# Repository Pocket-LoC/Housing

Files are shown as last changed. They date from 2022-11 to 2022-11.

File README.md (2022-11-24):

# Pocket LoC
 
Lab-on-chip (LoC) technology is becoming increasingly relevant, especially in the field of medicine. However, often LoC setups rely on complex lab equipment for operation. The aim of this project is to create an affordable and portable LoC setup as a proof-of-concept for truly pocket-sized LoC - the Pocket LoC.

Pocket LoC can be assembled with standard equipment found in a typcial engineering lab (such as a maker space or FabLab). Once assembled, Pocket LoC is fully portable and only needs a PC to operate.

## Housing
This repository contains the design files and instructions for the Pocket LoC housing as well as the assembly instructions and parts lists required for the complete setup.

Feel free to contact me if you interested in a complete Pocket LoC device.

### 3D-printed parts
The housing is designed for 3D-printing. Although many different options for materials and printer settings are possible, I achieved best results using PETG with a layer height of 0.2mm on an 'Original Prusa i3 MK3S+'. Most standard 3D-printers and materials (e.g. PLA or ABS) should work, although some adjustments of part tolerances may be necessary.

The housing was designed in FreeCAD ([CAD folder](https://github.com/Pocket-LoC/Housing/tree/main/CAD)). Ready-to-print models (.stl) can also be found in the CAD folder. All parts can be printed without support structures.

### List of parts and tools
- 3D-printer
- dark, opaque printing filament (e.g. [black PETG](https://www.prusa3d.com/product/prusament-petg-jet-black-1kg/)) (approx. 30€)
- [Pocket LoC Sensor](https://github.com/Pocket-LoC/Sensor) (approx. 65-90€)
- [Pocket LoC Pump Controller](https://github.com/Pocket-LoC/Pump-Controller) (approx. 50-75€)
- Metal rod or nail (approx. 1.7mm diameter) for the hinge
- 4x [Bartels mp6-liq Micropumps](https://darwin-microfluidics.com/collections/piezo-pumps/products/bartels-mp6-micropump) (128€)
- [Bartels Pump Driver](https://darwin-microfluidics.com/collections/piezo-pumps/products/mp-highdriver4-pump-driver) (159€)
- [Tubing](https://darwin-microfluidics.com/collections/silicone-tygon-tubing/products/mp-t-1-3-mm-tygon-tubing-for-bartels-micropumps) (9.50€)
- 4x [Luer Adapters](https://darwin-microfluidics.com/collections/luer-fittings/products/barbed-to-female-luer-adapter-for-1-16-1-8-and-3-32-id-soft-walled-tubing-pack-of-10?variant=32430390018184) (11.40€ for 10)
- 4x 3ml Syringes as reservoir (approx. 10€ for 100)
- [Microfluidic Chip](https://github.com/Pocket-LoC/Chip) (approx. 250€ for many chips)
- Tweezers

In total the Pocket LoC costs about 600-800€, depending on the choice of materials and manufacturers. The costs scale significantly lower for larger quantities.

### Assembly
1.  Print the housing parts found in the CAD folder:
      - Base
      - Lid
      - Reservoir holder
      - Reservoir fixation block (4x)
      - Chip fixation block (2x)
      - Sensor cover
      
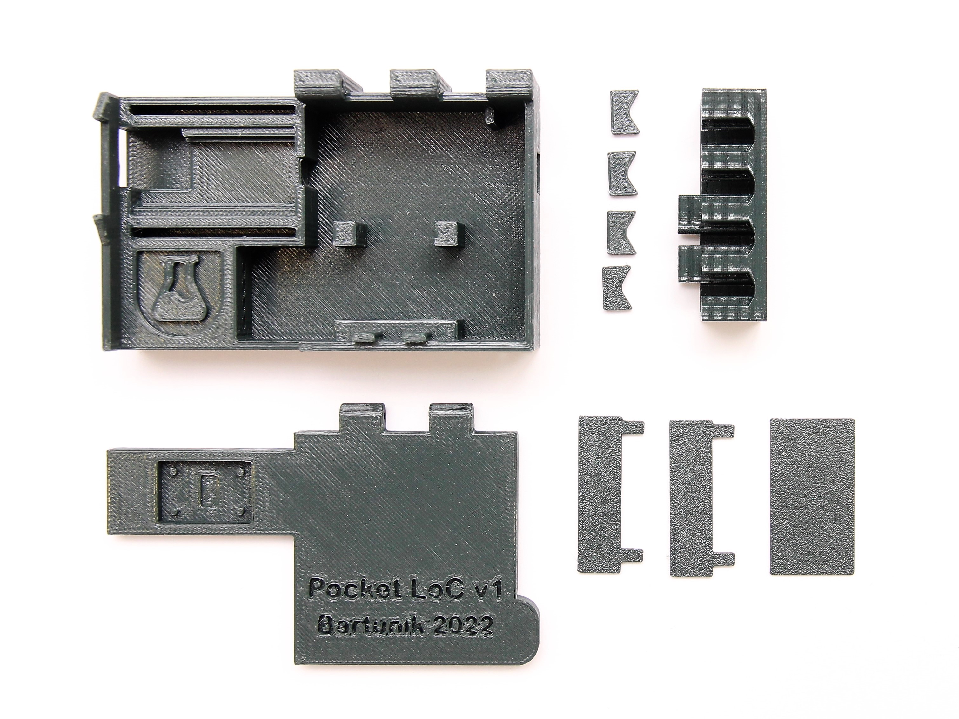
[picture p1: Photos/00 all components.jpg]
      
   
2. Fold the FFC as shown, about 25mm from one end and insert it into the connector on the LED PCB (part of the Pocket LoC sensor). Ensure the contacts of the FFC are facing outwards and the latch of the connector is properly fixed.

      <p float="left">
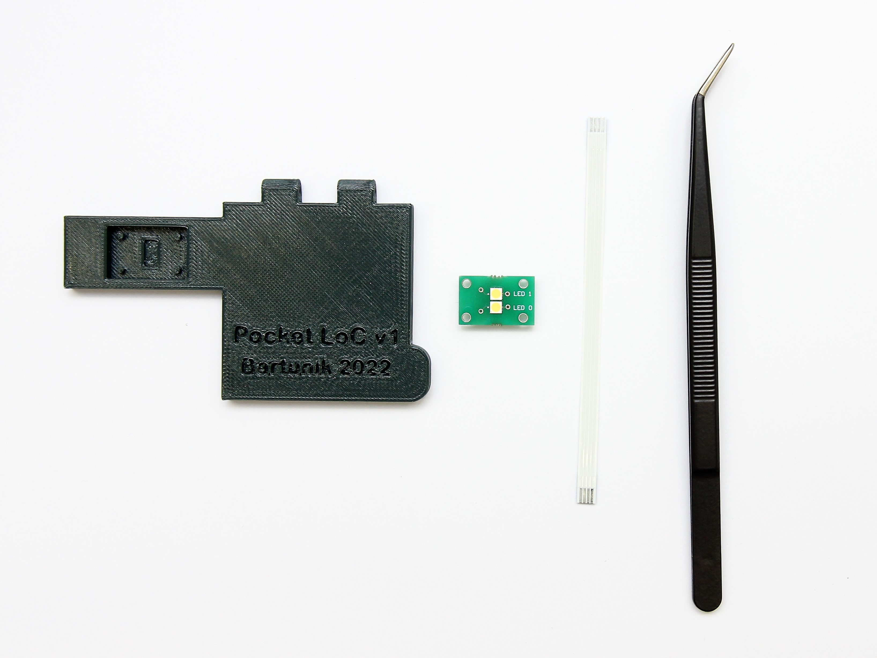
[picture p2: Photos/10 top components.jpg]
        
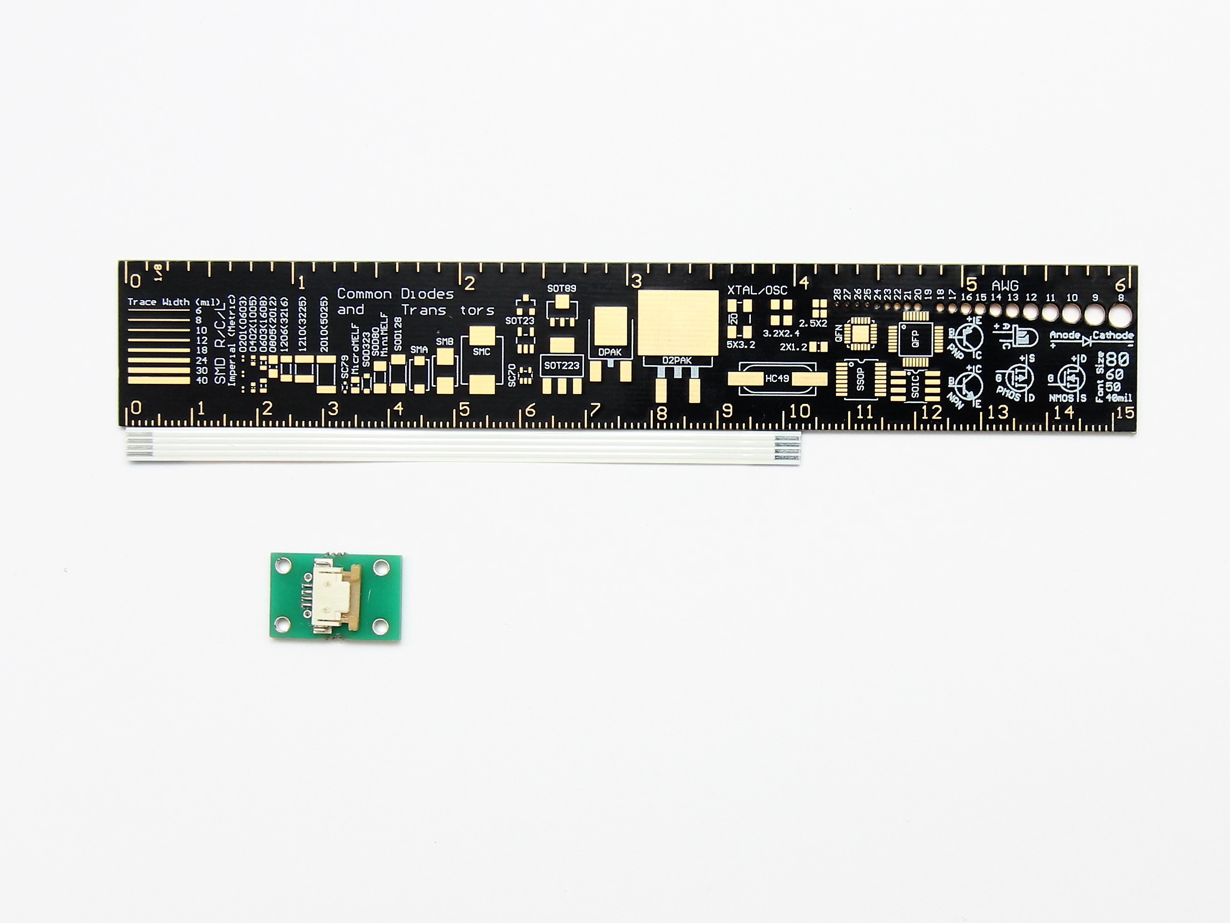
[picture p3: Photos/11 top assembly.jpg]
         
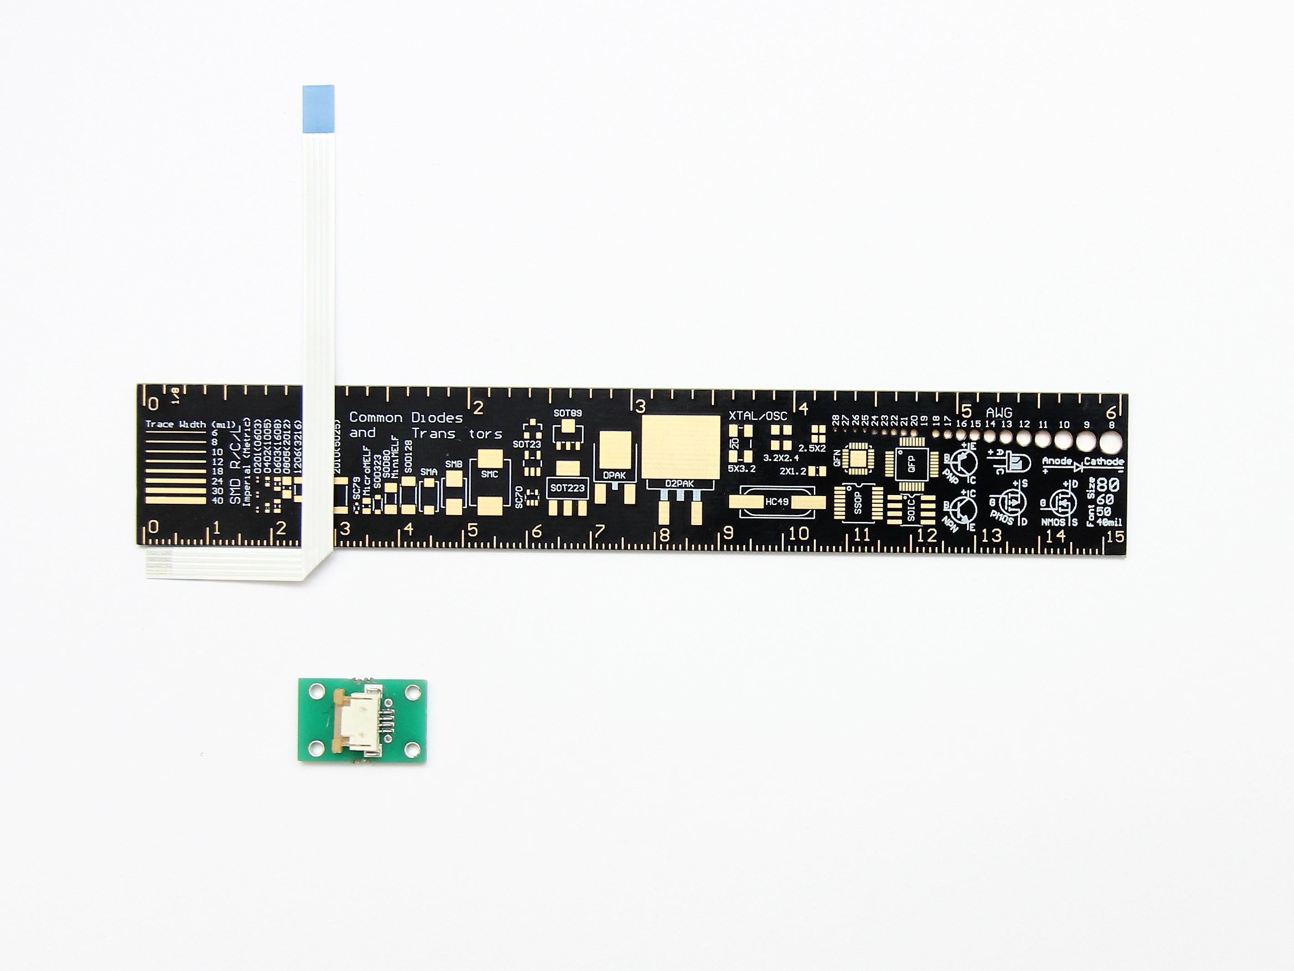
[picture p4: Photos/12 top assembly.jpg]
        
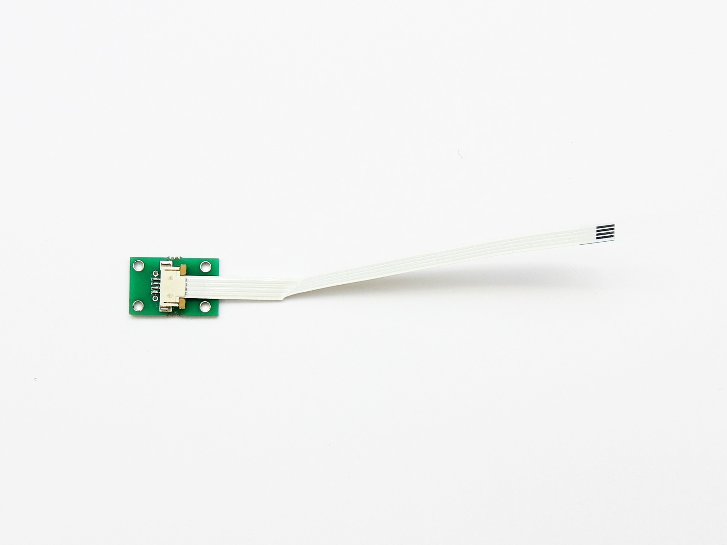
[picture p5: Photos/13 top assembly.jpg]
        
      </p>

3. Place the LED PCB in the top, threading the FFC through the hole and underneath the two holding bars. Tweezers may help with the last section.
      <p float="left">
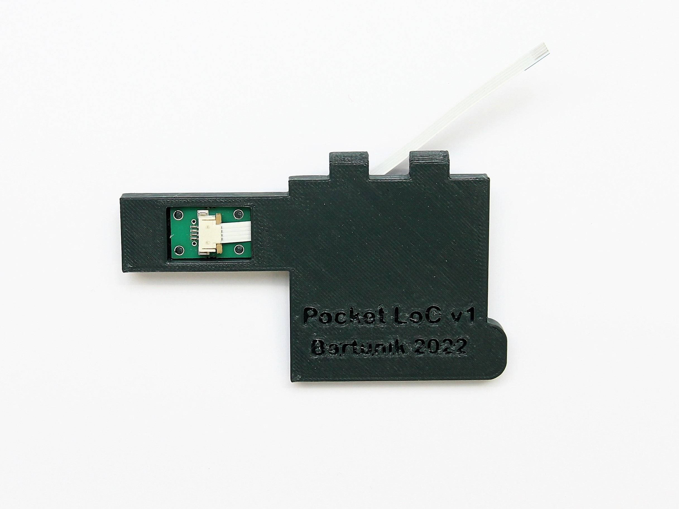
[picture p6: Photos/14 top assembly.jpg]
        
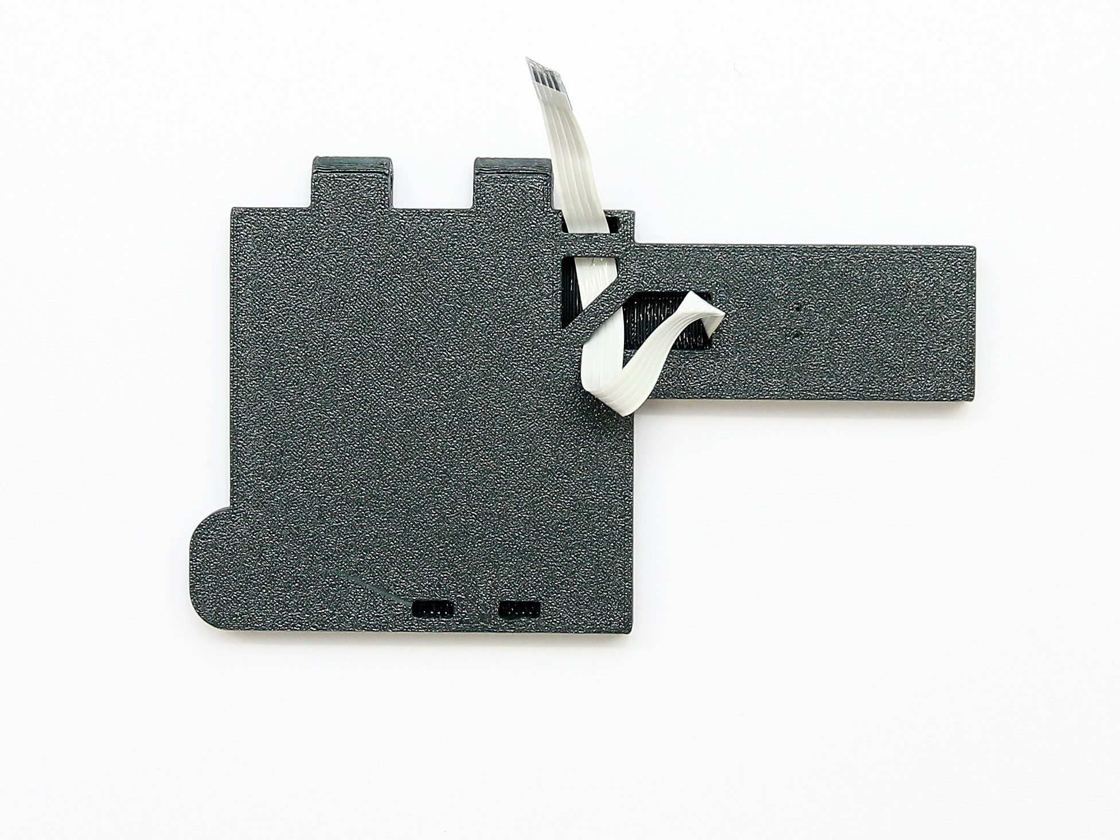
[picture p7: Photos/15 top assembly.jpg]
         
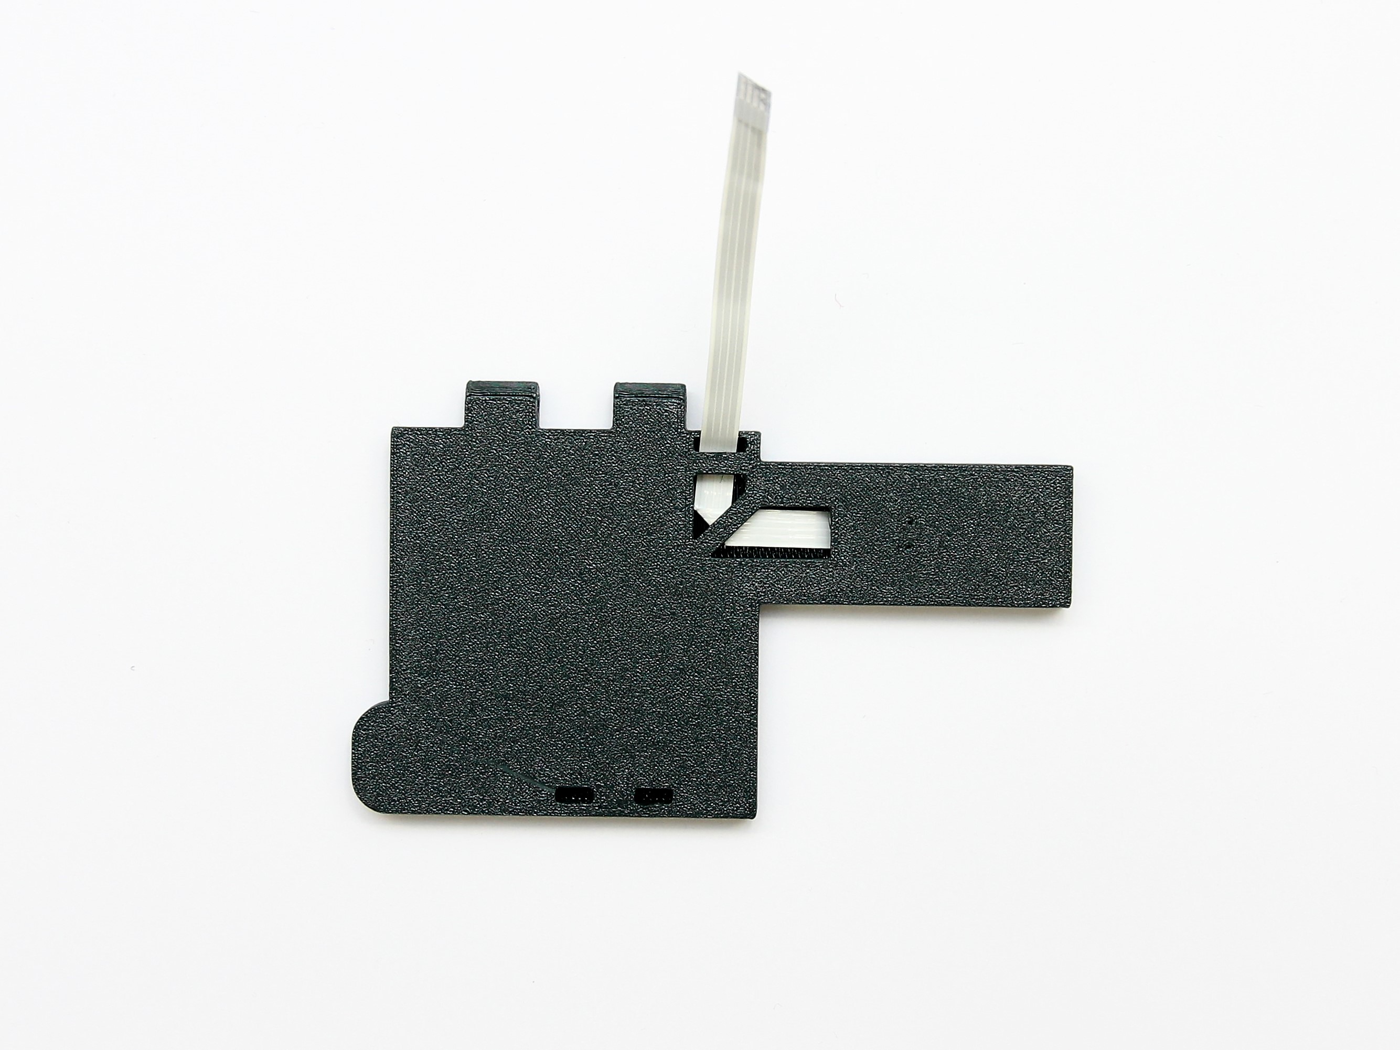
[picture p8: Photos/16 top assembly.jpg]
        
      </p>

4. Fold over the contact section of the FFC end. Then add a second fold, producing a Z-shape, at approx. 10 mm from the previous crease. Fold the FFC over at a right angle directly next to the last fold. Finally, add a crease approx. 15 mm from the outer edge of the angled fold. The folded FFC should look similar to the last picture.

      <p float="left">
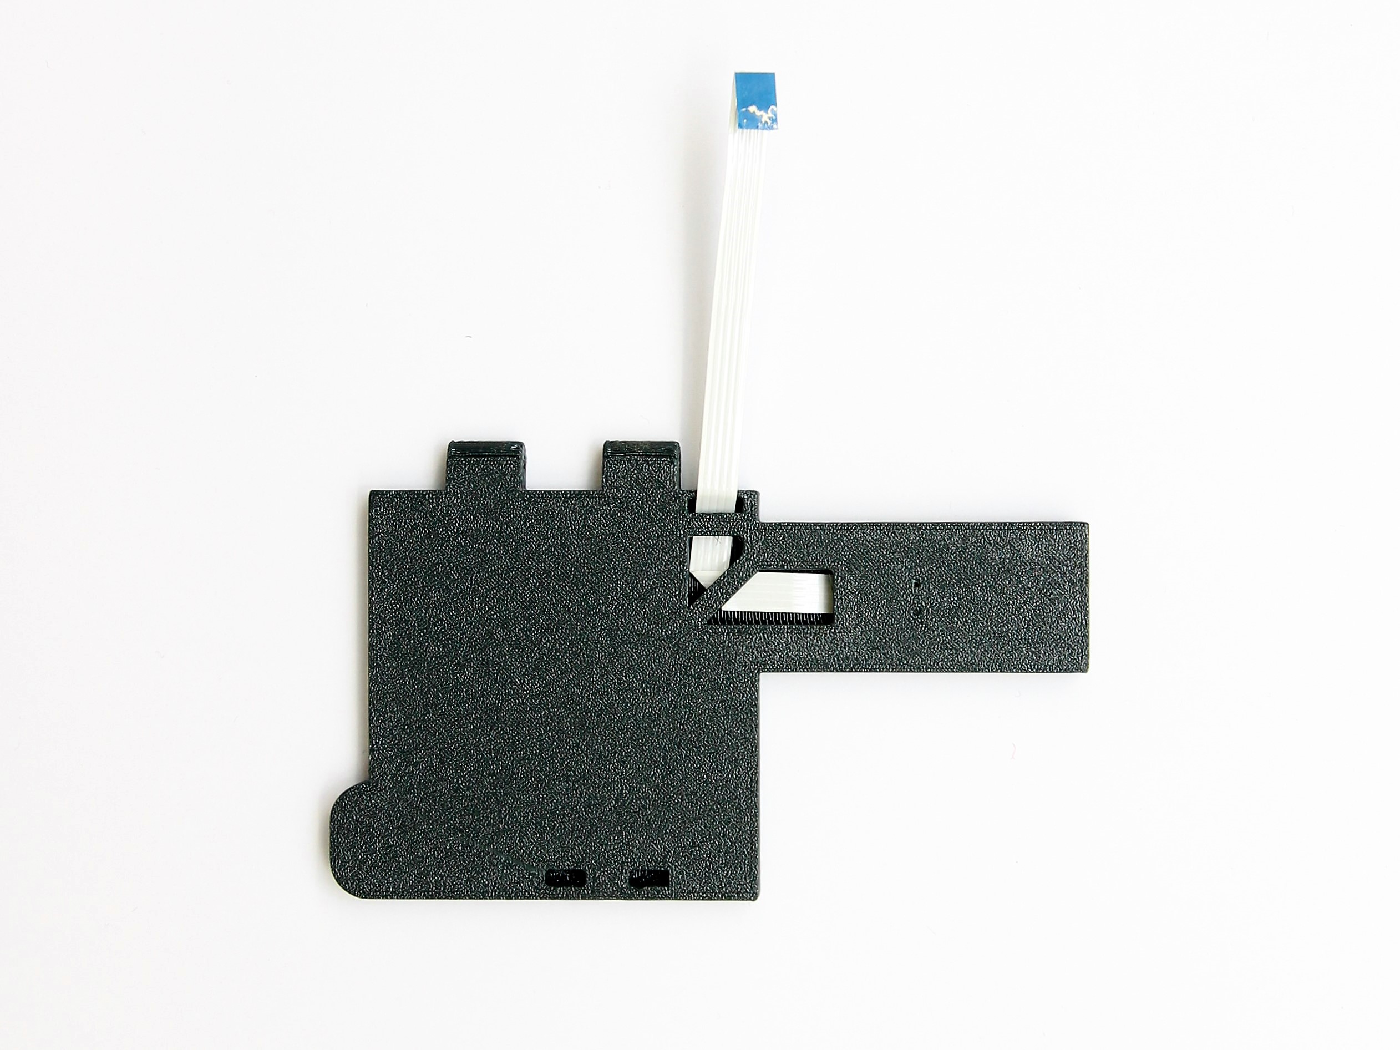
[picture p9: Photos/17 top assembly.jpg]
        
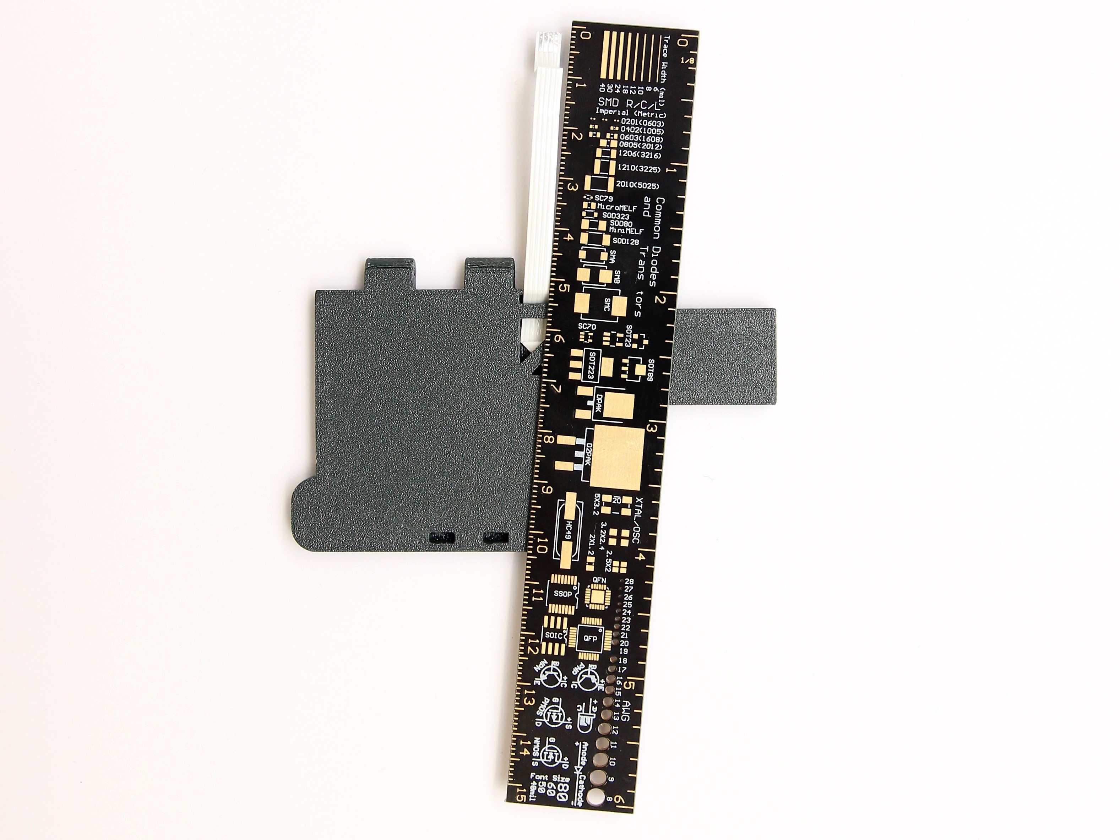
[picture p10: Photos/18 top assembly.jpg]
         
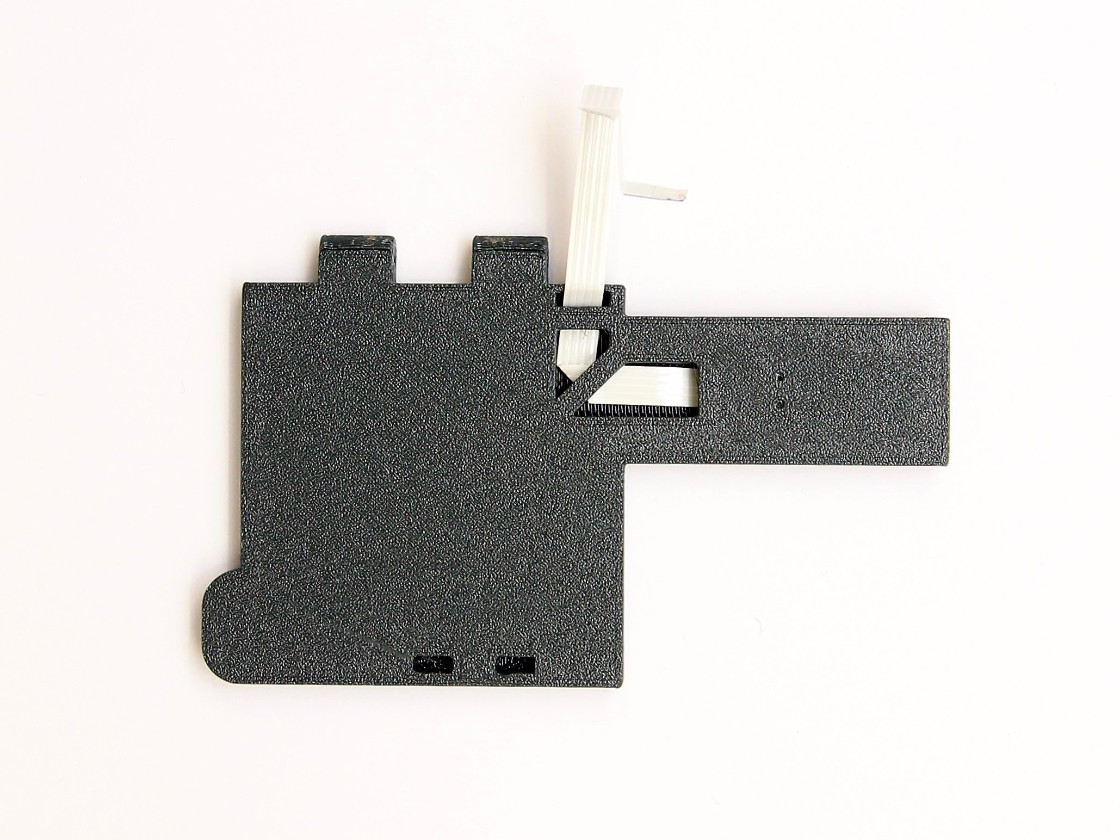
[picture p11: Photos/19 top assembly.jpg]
        
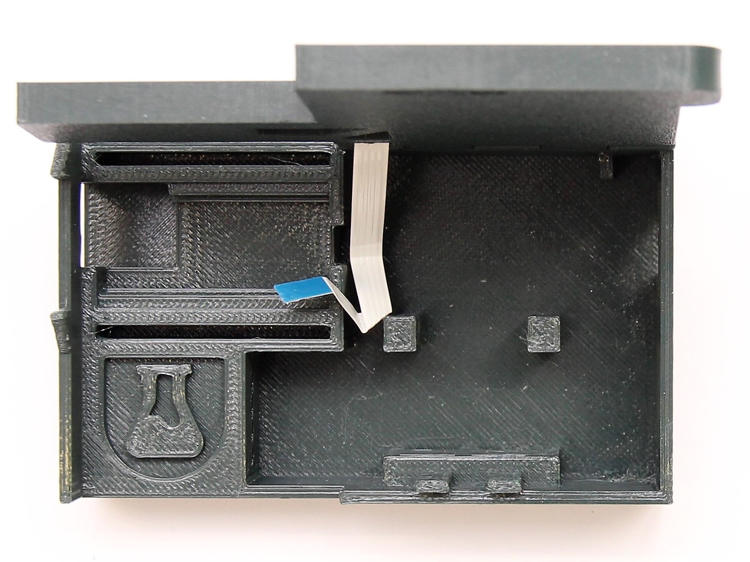
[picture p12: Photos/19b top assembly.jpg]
        
      </p>

5. Connect the base and lid by inserting the rod into the hinge section. A vice may help to push the rod in carefully.

      <p float="left">
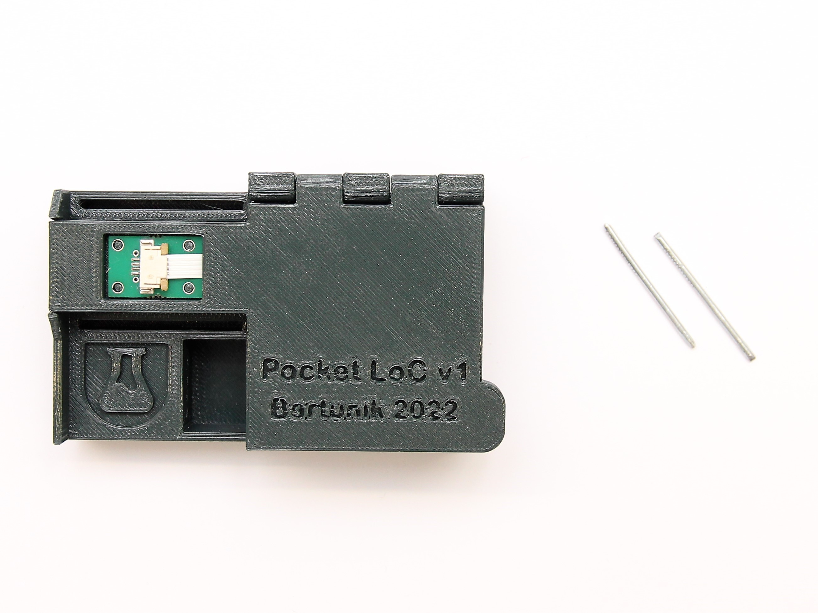
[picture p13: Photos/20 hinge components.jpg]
        
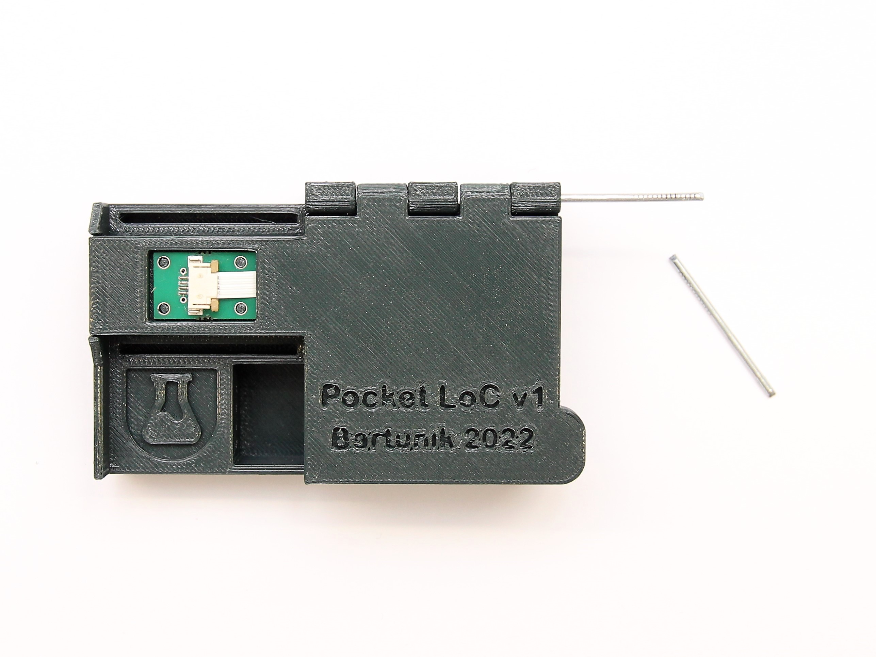
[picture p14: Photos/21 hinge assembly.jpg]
         
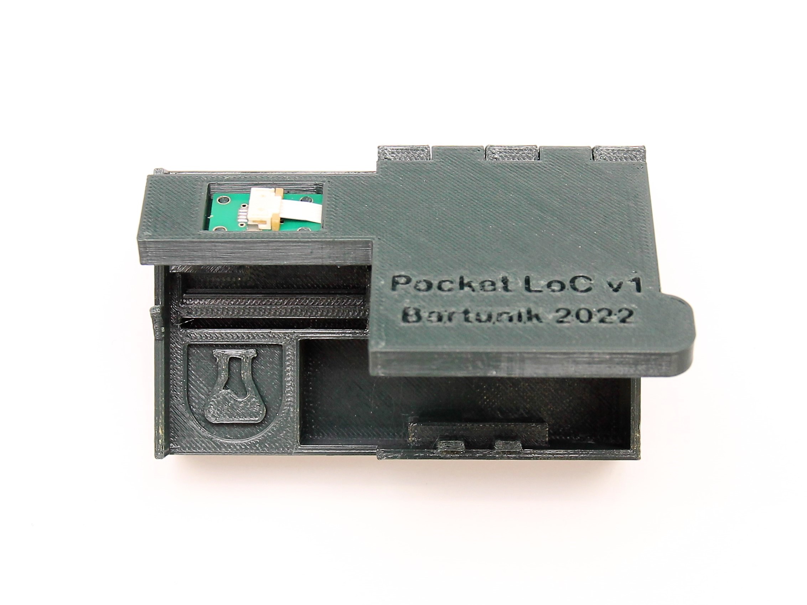
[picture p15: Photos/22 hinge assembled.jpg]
        
      </p>

6. Connect the sensor PCB to the FFC, again ensuring the contacts are facing outwards and the connector is properly fixed. Put the sensor in the base section with the USB and FFC connectors facing downwards and add the cover. Depending on your print quality, you may have to use a needle or thin drill to ensure the holes in the cover are clear from residue.

      <p float="left">
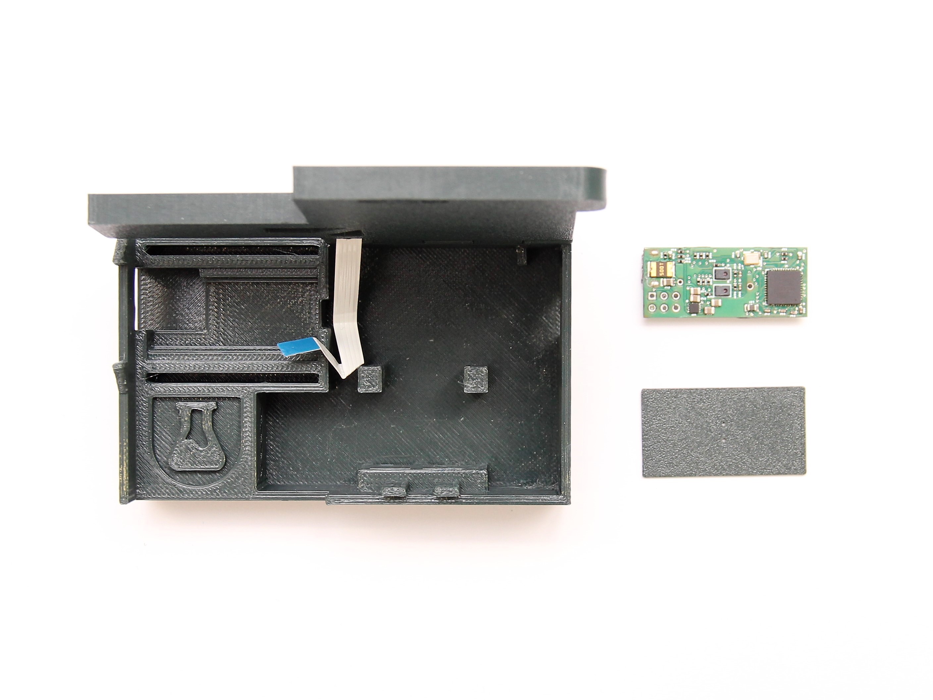
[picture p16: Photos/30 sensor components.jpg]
        
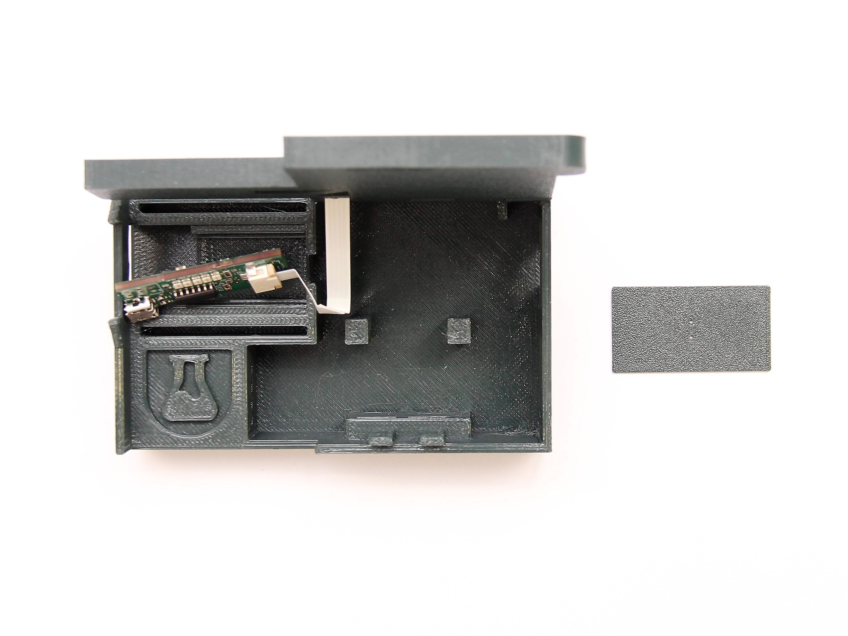
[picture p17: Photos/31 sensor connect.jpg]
         
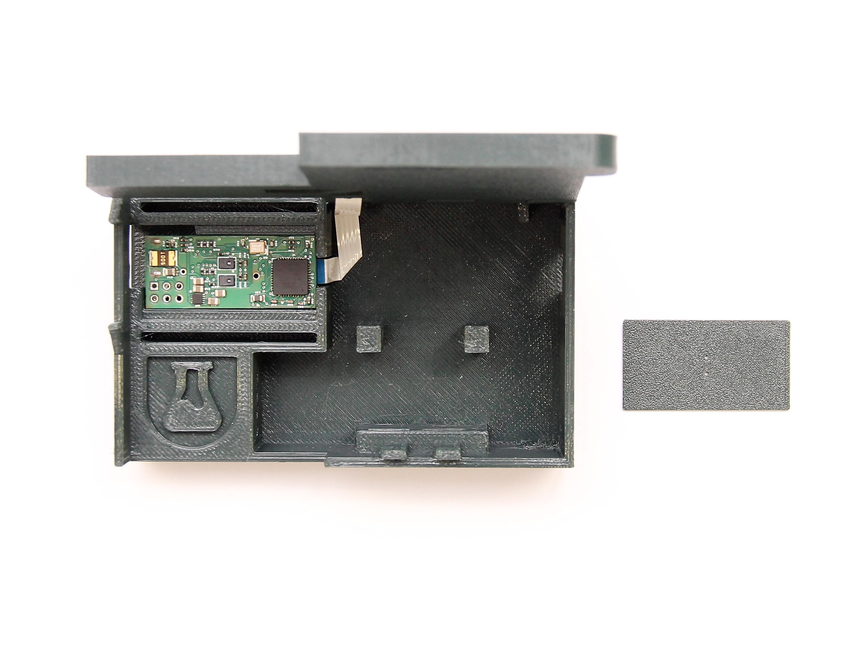
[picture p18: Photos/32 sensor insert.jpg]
        
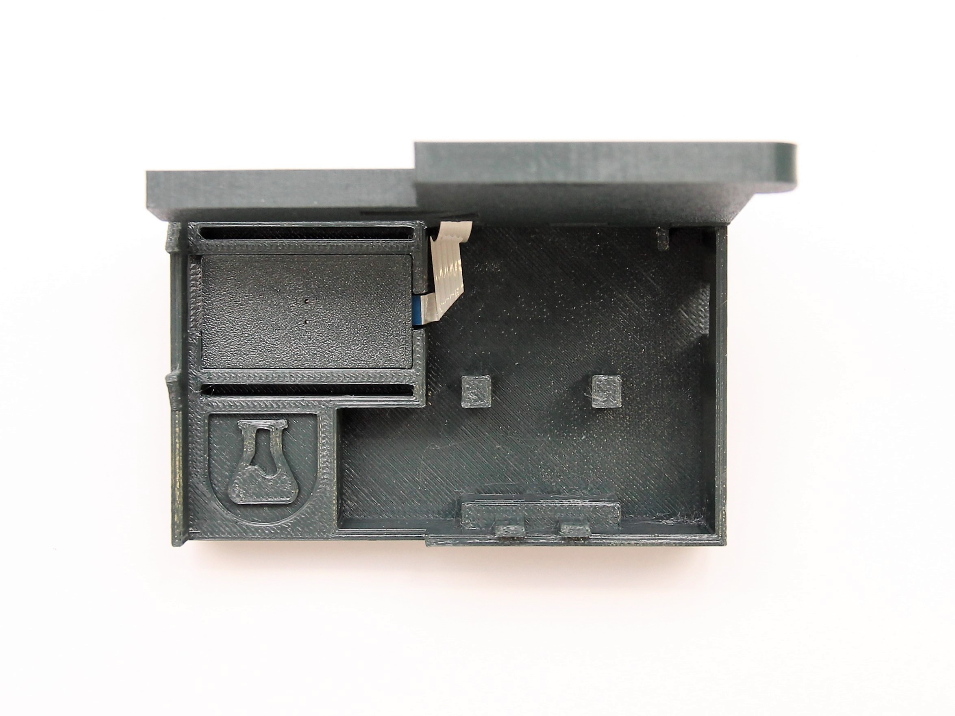
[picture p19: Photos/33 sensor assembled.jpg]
        
      </p>

5. Assemble the reservoir holder with four Luer adapters, some tubing, and the fixation blocks. First, connect the tubing to the Luer adapters, then place them in the reservoir holder and add the fixation blocks. The blocks should be flush with the surface of the reservoir holder.

      <p float="left">
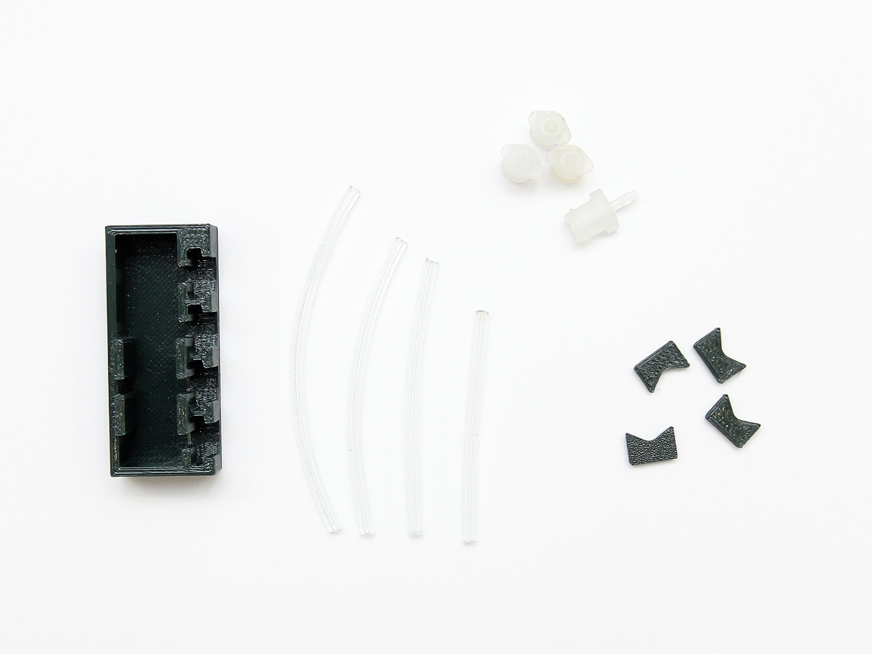
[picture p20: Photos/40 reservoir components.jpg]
        
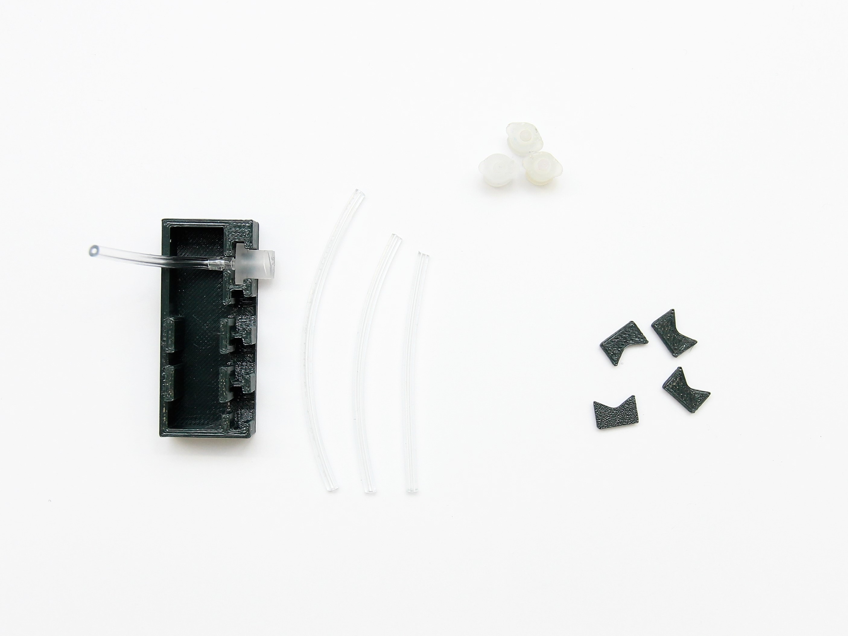
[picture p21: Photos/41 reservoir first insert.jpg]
         
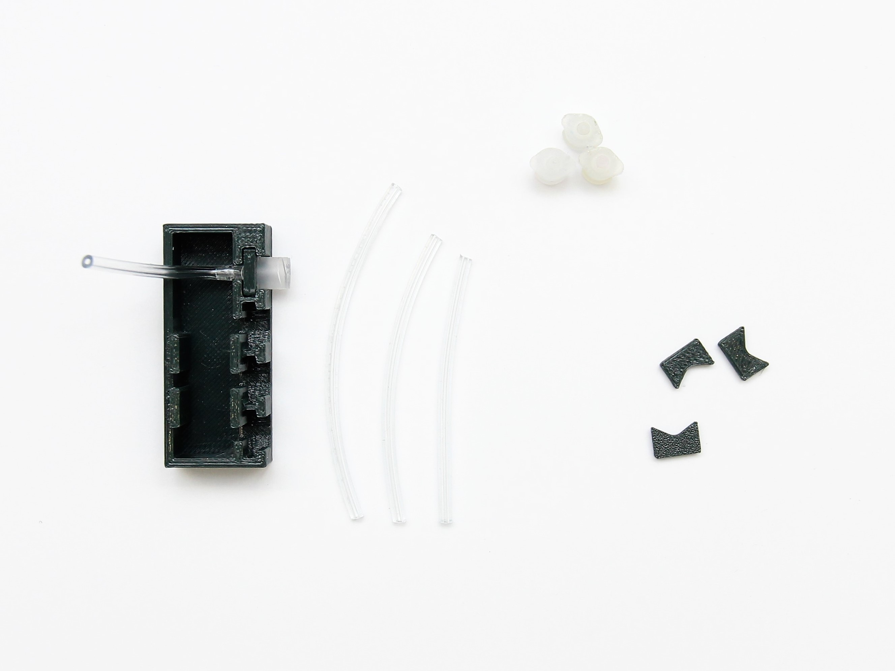
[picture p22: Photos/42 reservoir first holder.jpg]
        
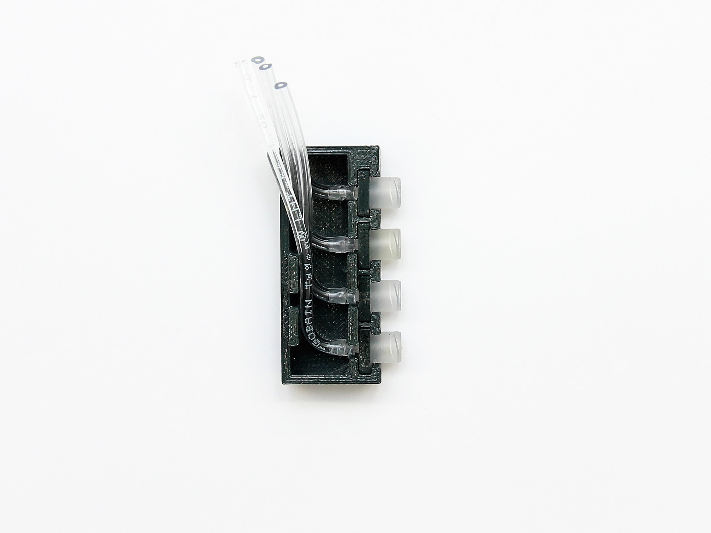
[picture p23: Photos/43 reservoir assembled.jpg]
        
      </p>

6. Connect the reservoir holder to the base section, threading the tubes through the holes on the side.

      <p float="left">
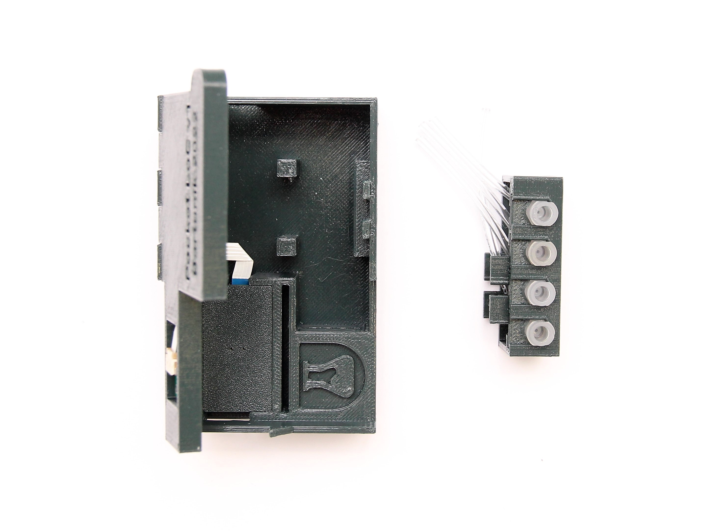
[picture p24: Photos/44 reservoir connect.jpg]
        
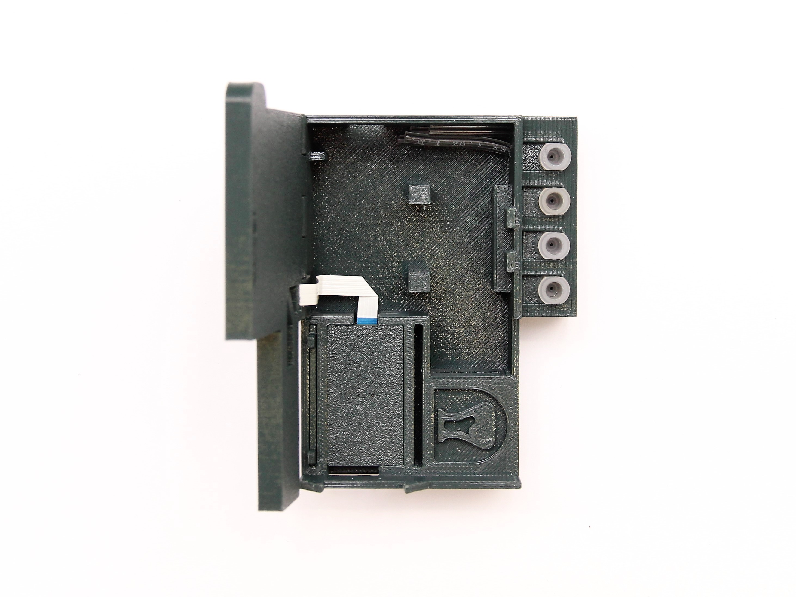
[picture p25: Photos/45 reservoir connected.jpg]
         
      </p>

7. Assemble the pump driver section, ensuring that the marked "PIN1" on the driver section (Bartels Highdriver-4) is aligned with the USB connector of the pump controller. Then insert the micropumps (Bartels mp6-liq), ensuring that the arrows are facing away from the USB connector, and close the connectors by pushing them down. Tweezers may help if you have to open the connectors again to remove the pumps.

      <p float="left">
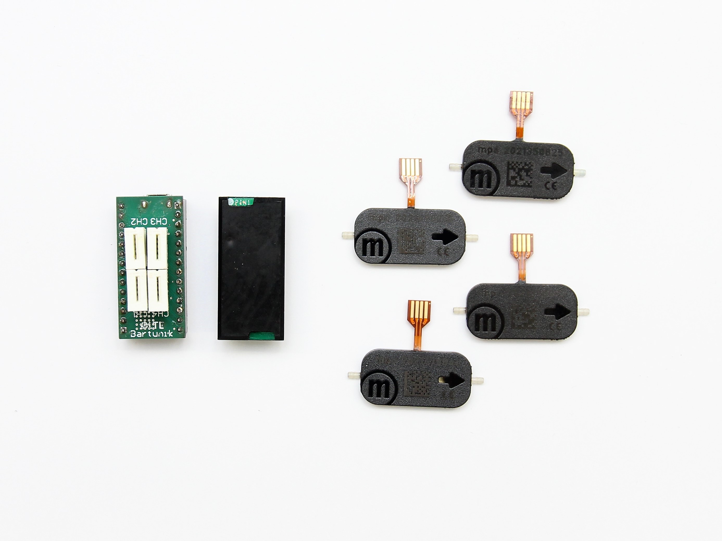
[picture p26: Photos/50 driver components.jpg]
        
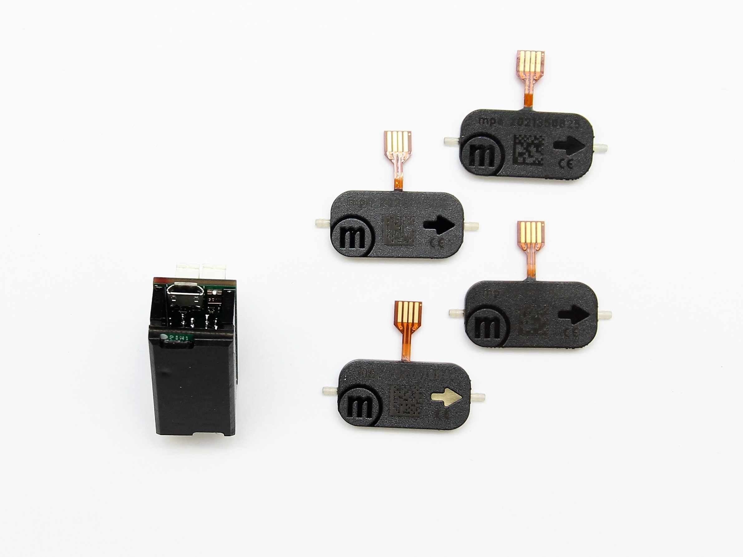
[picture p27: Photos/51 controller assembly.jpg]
         
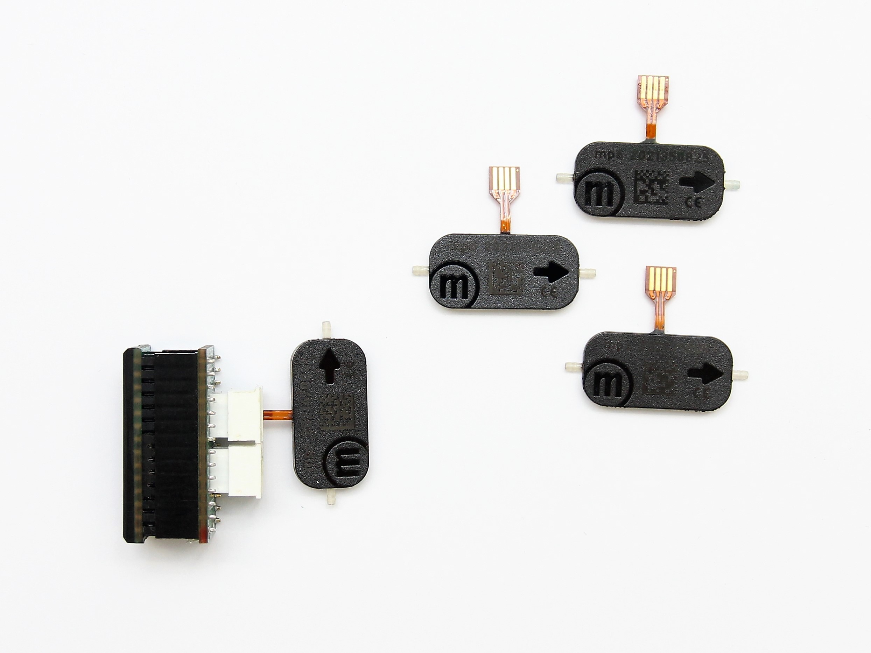
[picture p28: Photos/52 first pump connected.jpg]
        
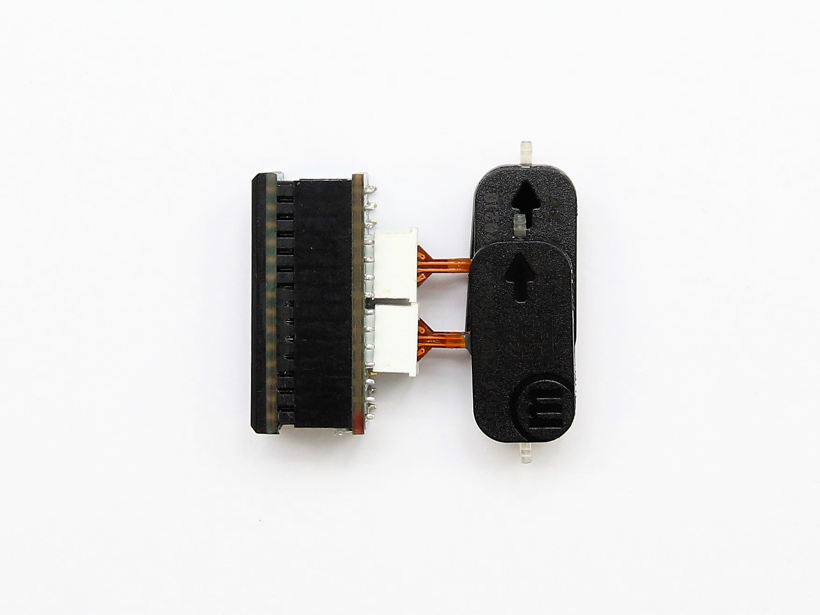
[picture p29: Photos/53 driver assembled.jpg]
        
      </p>
      
8. Insert the pump driver section into the base with the pump arrows facing the Pocket LoC logo. You will have to slightly bend the pump wires by pushing the pumps towards the controller. Connect the reservoir inlet and outlet tubing, which can be threaded through underneath the Pocket LoC logo. Again the tweezers may be useful here.

      <p float="left">
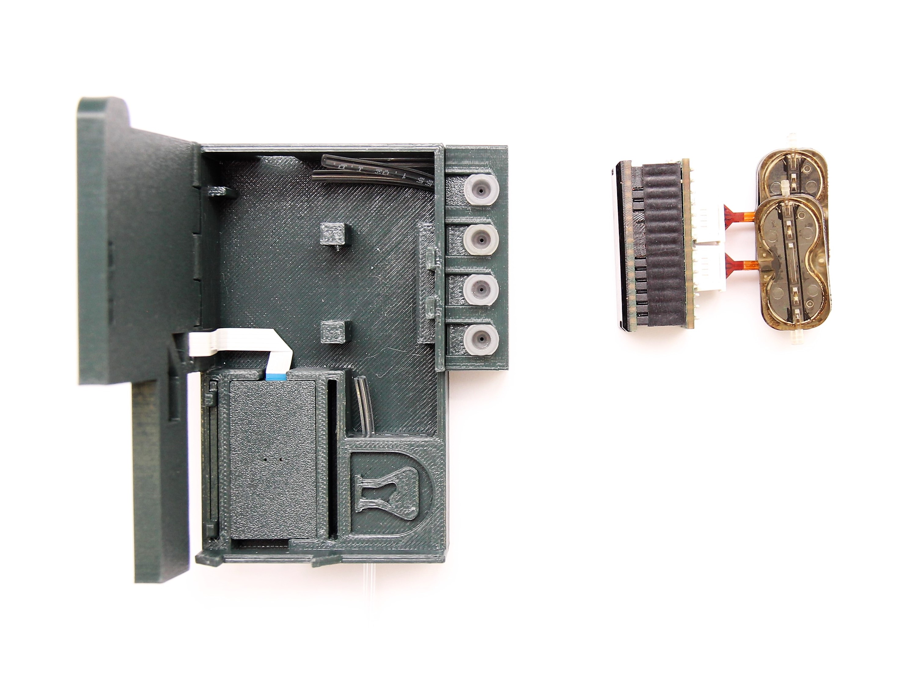
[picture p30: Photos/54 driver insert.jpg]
        
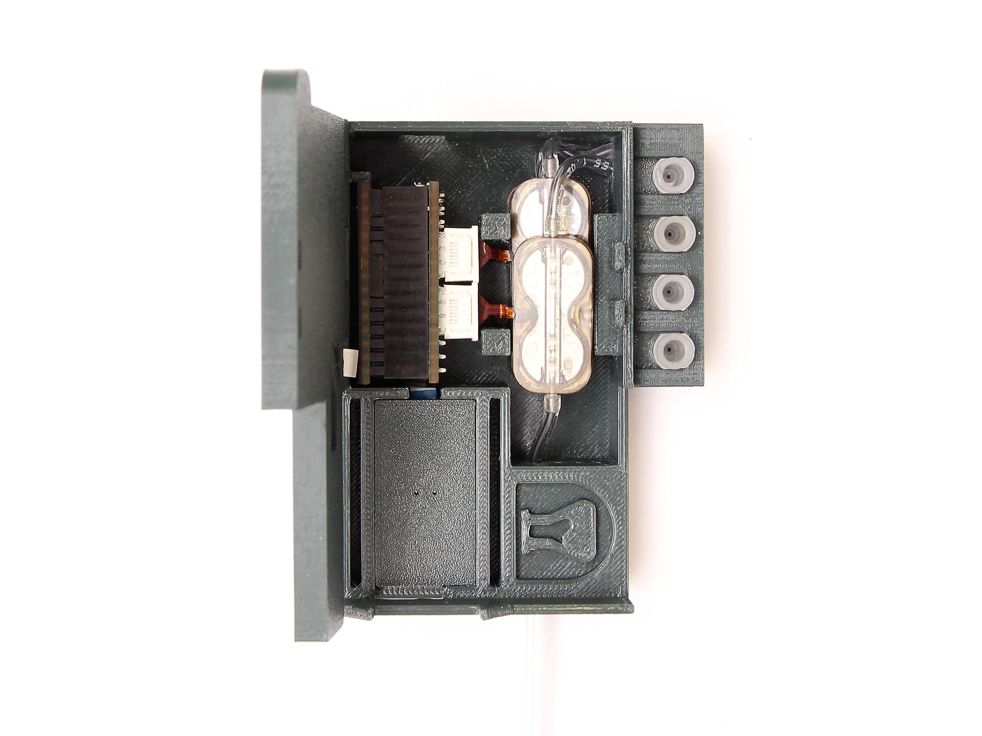
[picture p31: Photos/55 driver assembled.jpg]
         
      </p>

9. Insert the chip fixation blocks, used to align the microfluidic chip with the sensor aperatures. Depending on the size and layout of your microfluidic chip you may have to customise the blocks to fit your needs. The CAD folder contains samples for both a centered and one-sided chip placement.

      <p float="left">
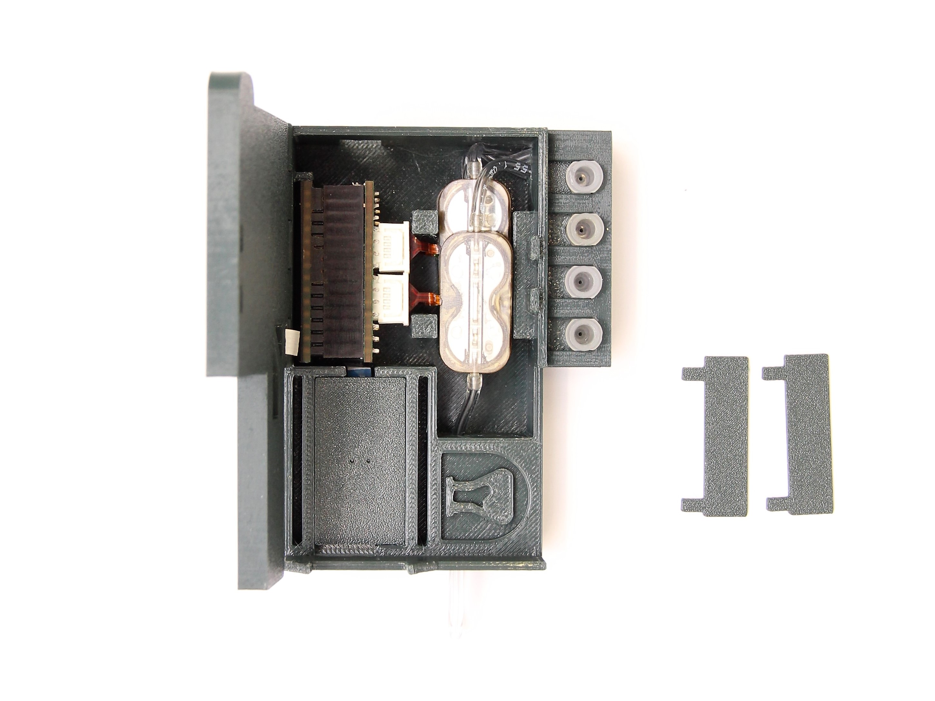
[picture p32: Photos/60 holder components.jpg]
        
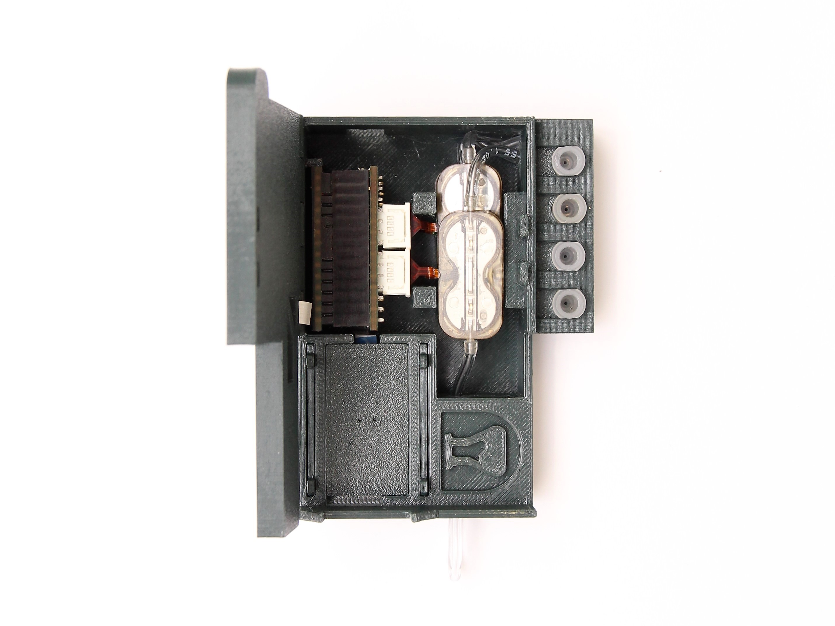
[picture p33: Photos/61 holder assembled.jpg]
         
      </p>

10. Finally, insert one USB cable each for the sensor and pump controller, connect to a PC and start your experiments. Some sample code is provided for both the sensor and pump controller in their repositories to help you get started. Your reagents can simply be connected through the Luer adapters. We suggest the use of 3ml syringes. In some cases you may produce better results if you remove the plungers from the syringes.

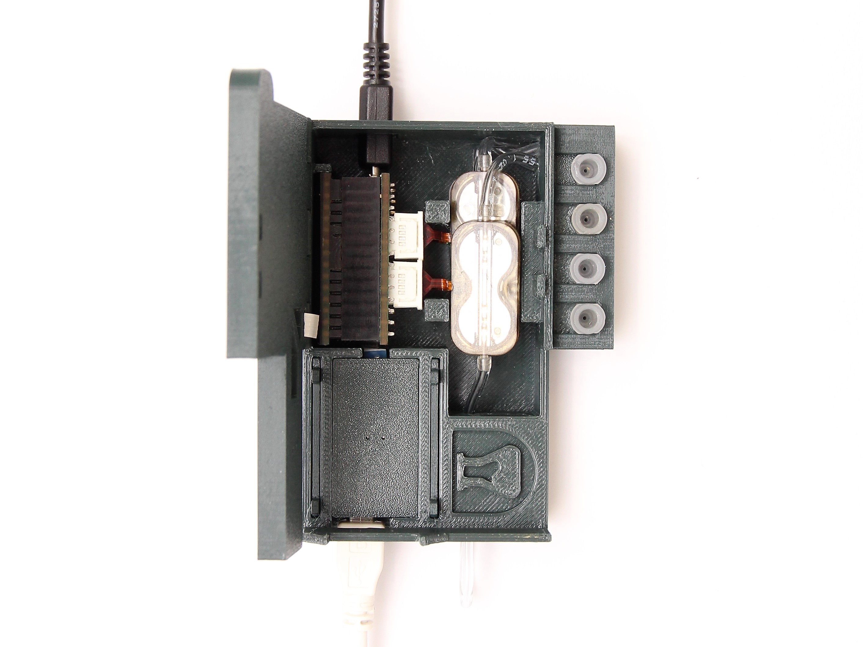
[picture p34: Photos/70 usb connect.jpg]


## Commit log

2022-11-16 Added CAD files
    [Housing.FCStd, Position Holders.FCStd, bottom.stl, position_holder_middle.stl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]
2022-11-17 Update CAD
    [Housing.FCStd, Position Holders.FCStd, position_holder_middle.stl, position_holder_side.stl]
2022-11-17 Add assembly pictures
2022-11-17 Create 19b top assembly.jpg
2022-11-25 Added font
    [Housing.FCStd]
